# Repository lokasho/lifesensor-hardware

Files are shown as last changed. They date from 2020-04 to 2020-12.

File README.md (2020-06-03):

# lifesensor-hardware
Temporary repository for the next hardware generation of the CADUS Life Sensor.
Official repository at https://github.com/cadus/Life-Sensor.

## Similar projects and Resources:
- https://github.com/GliaX
- https://github.com/kitspace/awesome-electronics
- https://github.com/kitspace/kicad_footprints
- https://github.com/intajay/open-electronics

- ecg
    + https://github.com/xdever/MobilECG-II -> based on ADS1298
    + https://www.olimex.com/Products/Duino/Shields/SHIELD-EKG-EMG/open-source-hardware
    + https://www.electronicdesign.com/power-management/article/21798161/choose-the-right-resistors-for-medical-applications

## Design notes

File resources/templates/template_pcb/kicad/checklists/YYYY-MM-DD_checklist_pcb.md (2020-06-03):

# check list
- [ ] this file is a copy of ./YYYY-MM-DD_checklist_pcb.md with YYYY-MM-DD replaced by todays date.
- [ ] Updating the PCB from the schematic does not introduce changes. If errors/warnings can be ignored, list them here with a reason why.
- [ ] The DRC report has been saved to ../manufacture/gerbers/COMPONENT_VARIANT_PCBNAME.rpt
- [ ] All remaining unconnected items in the DRC report are followed by a line starting witht "Accepted: ... ", explaining why the connection can be ignored.
- [ ] All remaining error messages in the DRC report are followed by a line starting witht "Accepted: ... ", explaining why the error/warning can be ignored.
- [ ] The full board name equals the .kicad_pcb file name without the extension and is visibly placed on one outer copper layer.
- [ ] The board revision is visibly placed on one outer copper layer.
- [ ] The board revision major is equal to the design revision of the schematics
- [ ] The board revision minor has been incremented compared to the last board release or is one if this is the first release (last: , now: )
- [ ] The footprints have been archived to ../lib_footprint.pretty after the pcb has been edited the last time (FILE -> Archive Footprints -> Archive Footprints to Existing Library. Then choose lib_footprint)
- [ ] The drill and drill map files have been saved to ../manufacture/gerbers
- [ ] The gerber files of all necessary layers have been plotted to ../manufacture/gerbers
- [ ] The board has been exported as .svg file to ../manufacture/images with the following settings:
    - select all layers that are exported es gerber files
    - Print Mode: Color
    - svg page size: "Board area only"
    - Pagination: All layers in a single file

# change log
| date       | revision | author (github name) | description                  |
|:-----------|:---------|:---------------------|:-----------------------------|
| 2020-04-26 | 1        | lokash               | Created checklist            |
| 2020-04-27 | 2        | lokash               | Improved error report checks |
| 2020-04-27 | 3        | lokash               | Export layout as svg         |

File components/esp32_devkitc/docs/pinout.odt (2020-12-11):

# ESP32 DEVKITC Pinout

### Inputs/ External Interrupts

SENS_INT_BPM, SENS_INT_SPO2, SENS_INT_ECG

DISP_INT_TOUCH

### Outputs

~SENS_RST_ECG, ~SENS_RST_BPM, ~SENS_RST_SPO2

~SENS_CS_ECG, ~SENS_CS_BPM,~SENS_CS_SPO2

DISP_CS_DISP, DISP_CS_TOUCH

### Display BUS on VSPI (speed optimized)

DISP_MOSI, DISP_MISO, DISP_SCLK

### Debug

JTAG_~TRST, JTAG_TMS, JTAG_TCK, JTAG_TDI, JTAG_TDO

### PROC

PROC_SDA, PROC_SCL

## External GPIOs via I2C GPIO Expander

SENS_START, EXPGPIO1, EXPGPIO2, EXPGPIO3, EXPGPIO4, EXPGPIO5, EXPGPIO6, EXPGPIO7

|GPIO|Input|Output|Notes|Function|

|0|pulled up|OK|outputs PWM signal at boot, is pulled high|~SENS_CS_BPM|

|1|TX pin|OK|debug output at boot ||

|2|OK|OK|Needs to be floating while being flashed; |~SENS_CS_ECG|

|3|OK|RX pin|HIGH at boot |DISP_CS_TOUCH|

|4|OK|OK||~SENS_CS_SPO2|

|5|OK|OK|outputs PWM signal at boot,VSPI_CS |DISP_CS_DISP|

|6|x|x|connected to the integrated SPI flash||

|7|x|x|connected to the integrated SPI flash||

|8|x|x|connected to the integrated SPI flash||

|9|x|x|connected to the integrated SPI flash||

|10|x|x|connected to the integrated SPI flash||

|11|x|x|connected to the integrated SPI flash||

|12|OK|OK|boot fail if pulled high;MTDI,HSPI_MISO|JTAG_TDI|

|13|OK|OK|MTCK, HSPI_MOSI|JTAG_TCK|

|14|OK|OK|outputs PWM signal at boot,MTMS, HSPI_CLK|JTAG_TMS|

|15|OK|OK|outputs PWM signal at boot,MTDO,HSPI_CS|JTAG_TDO|

|16|OK|OK||~SENS_RST_BPM|

|17|OK|OK||~SENS_RST_SPO2|

|18|OK|OK|VSPI_CLK|DISP_SCLK|

|19|OK|OK|VSP_MISO|DISP_MISO|

|21|OK|OK|I2C_SDA|PROC_SDA|

|22|OK|OK|I2C_SCL|PROC_SCL|

|23|OK|OK|VSPI_MOSI|DISP_MOSI|

|25|OK|OK||SENS_MOSI|

|26|OK|OK||SENS_MISO|

|27|OK|OK||SENS_SCLK|

|32|OK|OK||GPIOEXP_INT|

|33|OK|OK||~SENS_RST_ECG|

|34|OK||input only|SENS_INT_ECG|

|35|OK||input only|DISP_INT_TOUCH|

|36|OK||input only; SENSOR_VP|SENS_INT_BPM|

|39|OK||input only; SENSOR_VN|SENS_INT_SPO2|

|EN|||Connected to RTS, DTR reset circuit|JTAG_~TRST|

|3V3|||3.3V|SENS_3V3_DIG|

|EXT_5V||||5V_in|

|GND1,2,3|||GND|GND|

Orange Pins are strapping pins.

convert table to text with | as separator to paste into github

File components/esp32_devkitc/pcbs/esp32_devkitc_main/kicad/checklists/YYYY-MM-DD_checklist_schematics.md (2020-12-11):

# hints
1. All paths are refered to the kicad project directory.

# check list

- [ ] this file is a copy of ./YYYY-MM-DD_checklist_schematics.md with YYYY-MM-DD replaced by todays date.
- [ ] No subschematic name contains blank spaces (both sheet name and subschematic file name)
- [ ] the date of all schematic pages info is the the date of the last schematic edit
- [ ] the command `python ../../../../../resources/scripts/archive_symbols.py esp32_devkitc_main.pro` has been run to move all schematic symbols to the local library
- [ ] The design revision has been incremented compared to the last release (last: , now: )
- [ ] The ERC report has been saved to ../manufacture/schematics/esp32_devkitc_main.erc
- [ ] All remaining error messages in the ERC report are followed by a line starting with "Accepted: ... ", explaining why the error/warning can be ignored.
- [ ] The schematics have been plotted into ../manufacture/schematics/esp32_devkitc_main.pdf after the last edit.

# change log

| date       | revision | author (github name) | description                                |
|:-----------|:---------|:---------------------|:-------------------------------------------|
| 2020-04-26 | 1        | lokash               | Created checklist                          |
| 2020-04-27 | 2        | lokash               | Improved error report checks and add hints |
| 2020-04-28 | 3        | lokash               | Improved schematics plotted check          |
| 2020-04-29 | 4        | lokash               | Fixed project name templates               |
| 2020-08-25 | 5        | lokash               | include experiences from ecg_ads1292       |

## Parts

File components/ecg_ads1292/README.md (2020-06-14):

# lifesensor ecg_ads1292
The lifesensor ecg_ads1292 component provides a [ECG](https://en.wikipedia.org/wiki/Electrocardiography) frontent based on Texas Instruments [ADS1292](http://www.ti.com/lit/ds/symlink/ads1292.pdf).

WARNING: THIS COMPONENT DOES NOT PROVIDE ANY PROTECTION AGAINST ELECTRICAL SHOCKS! ALWAYS USE APPROPRIATE MEDICAL APPROVED POWER SUPPLIES! USE AT YOUR OWN RISK!

## Objectives
This component is developed to quickly provide a first ECG sensor that can deliver reference data for comparison with other self-developed and possibly cheaper ECG frontends. It will also provide the possibility to test other (software) components like the pulse detection and the lifesensors [sensor bus](../system/lifesensor_system.svg) with real data.
<!-- TODO: link to sensor bus description -->

To minimize the development effort integrated circuits that include all needed analog circuitry are chosen. The ADS1292 is chosen because in a search it was the cheapest one that can provide a three channel ECG found.

Due to the prototype characteristics the development of the ecg_ads1292 compontent is not focusing on low prizes, availability or repairability.

## Subcomponents

This component consists of one PCB [ecg_ads1292_main](pcbs/ecg_ads1292_main) and a [driver](firmware).

For a description of the development of the PCB see [pcbs/ecg_ads1292_main/docs/README.md](pcbs/ecg_ads1292_main/docs/README.md)

For a description of the driver see [firmware/README.md](firmware/README.md)

#### Board view
This is a view of the last released version of the board:

ecg_ads1292_main board view

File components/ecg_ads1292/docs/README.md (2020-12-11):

# lifesensor ecg_ads1292
This document describes the [ECG](https://en.wikipedia.org/wiki/Electrocardiography) component based on Texas Instruments integrated ECG front end [ADS1292](http://www.ti.com/lit/ds/symlink/ads1292.pdf).

**WARNING: THIS CIRCUIT DOES NOT PROVIDE ANY PROTECTION AGAINST ELECTRICAL SHOCKS! ALWAYS USE APPROPRIATE MEDICAL APPROVED POWER SUPPLIES! USE AT YOUR OWN RISK!**

---

## Objectives
This component is developed to quickly provide a first ECG sensor that can deliver reference data for comparison with other self-developed and possibly cheaper ECG frontends. It will also provide the possibility to test other (software) components like the pulse detection and the lifesensors sensor bus with real data.

## Features
To be continued.
<!-- TODO: add ecg_ads1292 features -->

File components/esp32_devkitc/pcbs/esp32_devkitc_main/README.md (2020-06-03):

This is the kicad project directory template for a single pcb.
Its structure is inspired by https://hackaday.com/2017/05/18/kicad-best-practises-library-management/

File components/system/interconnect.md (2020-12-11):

<# Interconnect

The interconnect is the main bus between the PCBs of the different components of the lifesensor.
It is based on the 40-pin Raspberry Pi header.

The idea is to use the Raspberry Pi as a test platform for all components.

Pins with numbers higher than 26 are reserved and should therefore be left unconnected.

**ATTENTION: The Raspberry Pi can only deliver 30mA at the 3.3V rail and 300mA at the 5V rail.**

| Pin| RaspberryPi      | LifeSensor       | Pin| RaspberryPi        | LifeSensor      |
|  -:| :--------------- | :--------------- | -: | :----------------- | :---------      |
| 1  | 3V3 power        | SENS_3V3_ANA     | 2  | 5V power           | SENS_5V_ANA     |
| 3  | GPIO2 (SDA)      | SDA              | 4  | 5V power           | SENS_5V_ANA     |
| 5  | GPIO3 (SCL)      | SCL              | 6  | GND                | GND             |
| 7  | GPIO4 (GPCLK0)   | SENS_BPM_DRDY    | 8  | GPIO14 (TXD)       | SENS_IO0        |
| 9  | GND              | GND              | 10 | GPIO15 (RXD)       | SENS_IO1        |
| 11 | GPIO17           | SENS_ECG_DRDY    | 12 | GPIO18 (PCM_CLK)   | SENS_SPO2_DRDY  |
| 13 | GPIO27           | SENS_START       | 14 | GND                | GND             |
| 15 | GPIO22           | SENS_RST_BPM_n   | 16 | GPIO23             | SENS_RST_ECG_n  |
| 17 | 3V3 power        | SENS_3V3_DIG     | 18 | GPIO24             | SENS_RST_SPO2_n |
| 19 | GPIO10 (MOSI)    | SENS_MOSI        | 20 | GND                | GND             |
| 21 | GPIO9 (MISO)     | SENS_MISO        | 22 | GPIO25             | SENS_CS_BPM_n   |
| 23 | GPIO11 (SCLK)    | SENS_SCLK        | 24 | GPIO8 (CE0)        | SENS_CS_ECG_n   |
| 25 | GND              | GND              | 26 | GPIO7 (CE1)        | SENS_CS_SPO2_n  |
| 27 | GPIO0 (ID_SD)    | RESERVED         | 28 | GPIO1 (ID_SC)      | RESERVED        |
| 29 | GPIO5            | RESERVED         | 30 | GND                | GND             |
| 31 | GPIO6            | RESERVED         | 32 | GPIO12 (PWM0)      | RESERVED        |
| 33 | GPIO13 (PWM1)    | RESERVED         | 34 | GND                | GND             |
| 35 | GPIO19 (PCM_FS)  | RESERVED         | 36 | GPIO16             | RESERVED        |
| 37 | GPIO26           | RESERVED         | 38 | GPIO20 (PCM_DIN)   | RESERVED        |
| 39 | GND              | GND              | 40 | GPIO21 (PCM_DOUT)  | RESERVED        |

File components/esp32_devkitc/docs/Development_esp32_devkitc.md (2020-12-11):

# Development of esp32_devkitc

## System interfaces of the esp32 component

The following figure shows the connections between the different components of the lifesensor:
System 
The esp32 component is in the middle of the graph and
has four interfaces:

- The **power bus** towards the power component,
- the **sensor bus** towards the ecg, spo2, and bp components,
- the **display bus** towards a possible small internal display, and
- the **processor bus** towards an Raspberry Pi that may drive a bigger internal or external display

The following sections describe each interface in more detail.
### Power bus
The esp32 component is provided with a 5V from the power component.
The esp32 component then provides a digital and a analog 3.3V rail, as well as a analog 5V rail and distributes these rails to components on the sensor and display bus.

In order to be able to use simple power circuits both the output current 
of the provided rails is limited 
- to 200mA for the analog 5V rail,
- to 150mA for the analog 3.3V rail, and
- to 50mA for the digital 3.3V rail.

If this limit is exceeded, some of the components must directly use the 5V supply from the main power component and generate their own rails if needed. (See power component for limits of that rail.)

The DevKit-C uses a ESP32-Wroom which requires 500mA from a 3.3V rail.
The 3.3V power rail is provided by the DevKit-C itself with a AMS1117-3.3 LDO that can deliver up to 1A. This is sufficient to power the ESP32-Wroom and the 200mA for external components.

The maximum total input current of the 5V power rail then calculates to
$$
I_{5V, in, max} = \overbrace{500mA}^{ESP32-Wroom} + \overbrace{200mA}^{3.3V extern} + \overbrace{200mA}^{5V extern} = 900mA
$$

For the 5V input and analog rails a broad range of 4.5V to 5.5V is allowed.
For the 3.3V analog and digital output rails a closer range between 3.2V and 3.3V must be provided.

### Sensor bus
The sensor bus is part of the main interconnect, which is described in more detail in [/components/system/interconnect.md](../../system/interconnect.md).

It is based on the Raspberry Pi HAT connector and provides
- analog 5V power rail (provided by the esp32 component)
- analog 3.3V power rail (provided by the esp32 component)
- digital 3.3V power rail (provided by the esp32 component)
- SPI bus 
  - with three chip select lines for the three sensors (SENS_CS_ECG_n, SENS_CS_SPO2_n, SENS_CS_BPM_n)
  - esp32 component is master
  - might be shared with esp32 display SPI bus via jumper (excluding chip select signals)
- a reset signal for each sensor (SENS_RST_ECG_n, SENS_RST_SPO2_n, SENS_RST_BPM_n)
- one start signal for all sensors
- an interrupt line for each sensor (SENS_ECG_DRDY, SENS_SPO2_DRDY, SENS_BPM_DRDY)
- two GPIO lines that can be used for signals between the esp32 component and costum sensors (SENS_IO0, SENS_IO1)
- an I2C bus (SENS_SDA, SENS_SCL)
  - that might be used by the processor bus (jumper/solder bridge on ESP32 component)

### Internal display bus
The Internal display bus provides the possibility to connect a display with low resolution directly to the stm32.
For this the following signals/rails are provided
- 5V or 3.3V power rail (switchable per jumper/solder bridge on ESP32 component)
- SPI bus with 
  - two chip selects for display and touch sensor (INTDISP_CS_DISP_n, INTDISP_CS_TOUCH_n)
  - ESP32 is master
  - might be shared with sensor SPI bus via jumper (excluding chip select signals)
  - an interrupt signal for the touch sensor (INTDISP_ISR_TOUCH)

### Processor bus
The processor bus is a single I2C bus with the ESP32 module as master and the
RPi as slave. The I2C bus is
- has signals PROC_SDA and PROC_SCL
- might use the interconnect (jumper/solder bridge on ESP32 component)

## Other connections of the esp32 component
Besides the four interfaces to other system components, the esp32 component needs other connectors, which are described in the following sections.

### JTAG Header
A 20 pin ARM JTAG header is connected according to https://raw.githubusercontent.com/gojimmypi/ESP32/master/images/myESP32%20DevKitC%20pinout.png

| DevKitC Pin | JTAG signal  | header pin |
|---|---|---|
| 3V3  | VTref | 1 |
| EN | nTRST | 5 |
| IO12 | TDI | 8 |
| IO14 | TMS | 10 |
| IO13 | TCK | 4 |
| (GND) | RTCK | 11 |
| IO15 | TDO | 6 | 
| GND  | GND | 3,9 (7)|

---
# ESP32 DEVKITC Pinout

### Inputs/ External Interrupts
SENS_INT_BPM, SENS_INT_SPO2, SENS_INT_ECG  
DISP_INT_TOUCH 

### Outputs
~SENS_RST_ECG, ~SENS_RST_BPM, ~SENS_RST_SPO2
~SENS_CS_ECG, ~SENS_CS_BPM,~SENS_CS_SPO2 
DISP_CS_DISP, DISP_CS_TOUCH  

### Display BUS on VSPI (speed optimized) 
DISP_MOSI, DISP_MISO, DISP_SCLK 

### Debug 
JTAG_~TRST, JTAG_TMS, JTAG_TCK, JTAG_TDI, JTAG_TDO

### PROC
PROC_SDA, PROC_SCL

## External GPIOs via I2C GPIO Expander
SENS_START, EXPGPIO1, EXPGPIO2, EXPGPIO3, EXPGPIO4, EXPGPIO5, EXPGPIO6, EXPGPIO7 

|GPIO|Input|Output|Notes|Function|
|---|---|---|---|---|
|0|pulled up|OK|outputs PWM signal at boot, is pulled high|~SENS_CS_BPM|
|1|TX pin|OK|debug output at boot ||
|2|OK|OK|Needs to be floating while being flashed; |~SENS_CS_ECG|
|3|OK|RX pin|HIGH at boot |DISP_CS_TOUCH|
|4|OK|OK||~SENS_CS_SPO2|
|5|OK|OK|outputs PWM signal at boot,VSPI_CS |DISP_CS_DISP|
|6|x|x|connected to the integrated SPI flash||
|7|x|x|connected to the integrated SPI flash||
|8|x|x|connected to the integrated SPI flash||
|9|x|x|connected to the integrated SPI flash||
|10|x|x|connected to the integrated SPI flash||
|11|x|x|connected to the integrated SPI flash||
|12|OK|OK|boot fail if pulled high;MTDI,HSPI_MISO|JTAG_TDI|
|13|OK|OK|MTCK, HSPI_MOSI|JTAG_TCK|
|14|OK|OK|outputs PWM signal at boot,MTMS, HSPI_CLK|JTAG_TMS|
|15|OK|OK|outputs PWM signal at boot,MTDO,HSPI_CS|JTAG_TDO|
|16|OK|OK||~SENS_RST_BPM|
|17|OK|OK||~SENS_RST_SPO2|
|18|OK|OK|VSPI_CLK|DISP_SCLK|
|19|OK|OK|VSP_MISO|DISP_MISO|
|21|OK|OK|I2C_SDA|PROC_SDA|
|22|OK|OK|I2C_SCL|PROC_SCL|
|23|OK|OK|VSPI_MOSI|DISP_MOSI|
|25|OK|OK||SENS_MOSI|
|26|OK|OK||SENS_MISO|
|27|OK|OK||SENS_SCLK|
|32|OK|OK||GPIOEXP_INT|
|33|OK|OK||~SENS_RST_ECG|
|34|OK||input only|SENS_INT_ECG|
|35|OK||input only|DISP_INT_TOUCH|
|36|OK||input only; SENSOR_VP|SENS_INT_BPM|
|39|OK||input only; SENSOR_VN|SENS_INT_SPO2|
|EN|||Connected to RTS, DTR reset circuit|JTAG_~TRST|
|3V3|||3.3V|SENS_3V3_DIG|
|EXT_5V||||5V_in|
|GND1,2,3|||GND|GND|

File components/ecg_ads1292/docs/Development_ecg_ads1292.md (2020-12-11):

# Development lifesensor ecg_ads1292

## Requirements and constraints
To minimize the development effort integrated circuits that include all needed analog circuitry are chosen. The ADS1292 is chosen because in a search it was the cheapest one that can provide a three channel ECG.
Due to the prototype characteristics the development of the ecg_ads1292 compontent is not focusing on low prizes, availability or repairability.

## Subcomponents
This component consists of one PCB [ecg_ads1292_main](../pcbs/ecg_ads1292_main) and a [driver](../code).

## PCB ecg_ads1292_main Rev. 0

### Schematics
The schematics can be found in 
../pcbs/ecg_ads1292_main/manufacture/schematics

The main sources for the circuit design are
- the ADS1292 data sheet: http://www.ti.com/lit/ds/symlink/ads1292.pdf
- TI Bio-Signal Monitor Reference Design: https://www.ti.com/tool/TIDM-BIOSIGNMONITOR
- the ADS1x9xECG-FE Demonstration Kit User's Guide: https://www.ti.com/lit/ug/slau384a/slau384a.pdf

The development of the circuits is straight forward as the ADS1292 only needs a few passive components and an optional LDO for the analog frontend, and a few others for connecting it to the [sensor bus](../../system/interconnect.md). Most components can be directly derived from the data sheet or the other links given above.

Nevertheless the following  will describe the circuits and components that differ from the references.

#### Analog input section
The input filter of the analog inputs IN1 to IN3 of the ADS1292R was derived from the Texas Instruments [demo board](http://www.ti.com/tool/TIDM-BIOSIGNMONITOR).
The input resistors R9 to R22 values have been decreased from 51kΩ to 22kΩ to compensate for the external defibrillator input protection.
Also the circuit has been changed so that each of three leads of the Einthoven triangle can be directly conected to one of the three input channels.
(Note however that only two leads can be measured directly, as the ADS1292 only comprises two ADCs. The third lead can be calculated from the other two).
The reason is, that if one electrode is torn off, the software can always switch to an input that is connected to the remaining two electrodes.
This way at least one valid lead can be measured in this case.

#### Right leg driver (*1*)
The wiring of the right-leg driver has also been adapted from th demo board. 
The Right-Leg-Driver is an OPV integrated in the ADS1292R, whose output (pin 30) is connected to an electrode on the patient via a resistor that will be included with the defibrillator protection. 
Therefore on this board the limiting output resistor was omitted.
To make the RLD compliant to the current limits (body floating, single fault codition -> max. 50µA DC according to wikipedia) an 100kΩ resistor R13 is inserted at the OPA output. On the demo board a 0Ω bridge is used at this point.
The idea for the circuit modification was taken from the Texas Instruments application report 'Improving Common-Mode Rejection Using the Right-Leg DriveAmplifier' ( www.ti.com/lit/an/sbaa188/sbaa188.pdf ). So if RLDOUT should be fully driven in case of an error, the output current is still limited by R13.
Due to the characteristics of the OPV, the potential between the resistors, i.e. at the connectors RLD output, is the same in both cases.
Since it is determined solely by the resistor R12 connected to the inverting input RLDINV.
In the real circuit, this means that the output of the OPV needs higher output voltage swing and has higher distortions.
Since the output current of the OPV is usually 1μA according to the Application Report, R13 leads to an additional voltage swing of 0.1V in the present circuit.
The disadvantages mentioned above should therefore be negligible.
As a result, the output impedance of the right-leg driver can be lowered.
It can be assumed that this will result in a higher cut-off frequency and a better response of the right-leg driver.

#### Analog power supply
To keep the analog power supply as quiet as possibly during prototyping and testing an additional LDO is inserted.
This can be ommitted after testing.

#### Analog frontend connection
The analog frontend will be connected to an external defibrillator protection circtuit.
To keep the ground connection between the two PCBs flexible the GND pins of Connector J1 have their own GNDPWR net, which can be connected to the GND net via several solder bridges at different points.

#### Sensor bus connection

A few notes about the sensor bus connection:
- no external Clock is required, therfore the CLKSEl pin is pulled high and the CLK pin is left unnconnected
- The GPIOs are not needed. The data sheet recommends to pull them down, which is down with two 6.8kΩ resistors.
- All digital output signals have a 100Ω series resistor to improve EMI. 
  TODO: evaluate signal quality in real environment.

The following list describes the nets of the sensor bus this component accesses.

**Power**

| Label           | Pin| Pi Header          |
|:----------------|:---|:-------------------|
| SENS_5V_ANA     | 2  | 5V power           |
| SENS_3V3_DIG    | 17 | 3V3 power          |

**Signals**

| Label           | Pin| Pi Header          |
|:----------------|:---|:-------------------|
| SENS_ECG_DRDY   | 11 | GPIO17             |
| SENS_START      | 13 | GPIO27             |
| SENS_RST_ECG_n  | 16 | GPIO23             |
| SENS_MOSI       | 19 | GPIO10 (MOSI)      |
| SENS_MISO       | 21 | GPIO9 (MISO)       |
| SENS_SCLK       | 23 | GPIO11 (SCLK)      |
| SENS_CS_ECG_n   | 24 | GPIO8 (CE0)        |

- **SENS_ECG_DRDY** Data ready. Is pulled down by the ADS1292 when a new sample has been taken. -> **ESP:** Interrupt on the falling edge, that triggers fetching the sample via SPI bus.
- **SENS_START** After configuring the continuos conversion mode the ADS129 starts sampling, when this signal is pulled HIGH. -> **ESP:** output push pull
- **SENS_RST_ECG_n** After system start the ADS1292 needs two reset pulses by driving this signal LOW. **ESP:** output push pull
- **SENS_MOSI** SPI bus
- **SENS_MISO** SPI bus
- **SENS_SCLK** SPI bus clock, maximum frequency is twice the ADS1292 base clock, so 1.024MHz when running on the internal 512kHz clock. **ESP:** (clock polarity: low, phase: second edge)
- **SENS_CS_ECG_n** SPI chip select for the ECG (no inter byte pulses, after transmitting data, this signal must not be driven HIGH agian to fast, see data sheet for SPI timing constraints)

### Layout

The constraints for the layout are
- 2 Layer
- best signal quality
- form factor (maximum) and mounting holes for RPi HAT:

<p>

(see sensor stack)

</p>

---

The board is not intended to be etched by a maker space or hobbyist, therefore vias and small structures can be used.
For the layout the hints in the datasheet are followed.
It states that the GND plane could be split, if the star point is at the ADS1292, but in general this is not neccessary with correct component placement and routing.
In this case a split is done, to keep the analog GND plane small to avoid coupling as the environement is not yet known.

Here is a view of the layout:
<p>
layout of ecg_ads1292_main
</p>

(*1*) This section is based on the translation of a project documentation at Technische Universität Berlin

### Start-up of first prototypes Rev. 0.1

Two prototypes have been produced July 2020.
As no LDO where ordered the analog supply voltage is directly using the 5V from the interconnect. This is done by shorting the appropriate pads for the LDO. (The ADS1292 allows the analog supply voltage to be 5V).

For the first tests a STM32 based NUCLEO-L476RG dev board was used.
Both power and digital signals where connected to that board.
The test program streams the data via UART to the included virtual serial port of the NUCLEO-L476RG which is connected to a PC.

To test the boards, the internal test signals of the ADS1292 are used.
With prototype 1 also a real ECG signal was successfully recorded.

#### Prototype 1
The tests show that the internal 2.4V reference voltage is not stable.
This leads to intermittent changes in the measured signal: at somw point they start to drift and sometimes saturate shortly just before recovering again.

After switching to the 4V reference these issues are gone. This is (only) possible because a 5V analog supply voltage is used.
This means that
**the 2.4V reference voltage of prototype 1 can not be used.**

While recording the real ECG signal the host PC (notebook) was detached from the mains adapter for safety reasons.
The result was visually ok. One channel had a little bit more noise which is due to the RLD input not beeing connected to one of the inputs of that channel. This can be improved at a later point.

#### Prototype 2
This device worked as expeceted.
But while testing the external analog input circuits, the signals saturated. The reason was, that the 2.4V internal reference was used, but the RLD pushes the potential to $V_{DDA} / 2 = 5V / 2 = 2.5V$, which is then outside  of the ADC range.
It should therefore be noted that, when using 5V as analog supply voltage, the internal reference voltage must be set to 4V or the RLD reference voltage must be supplied from an external voltage devider that provides a voltage below 2.4V (ideally 1.2V).

## ESP32 component driver 
The main IC ADS1292 needs to controlled from the ESP32 via SPI and several IO/interrupt lines.
The following describes the development of the driver.

To be continued.

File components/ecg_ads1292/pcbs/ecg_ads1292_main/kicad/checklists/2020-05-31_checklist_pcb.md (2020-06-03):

# check list
- [x] this file is a copy of ./YYYY-MM-DD_checklist_pcb.md with YYYY-MM-DD replaced by todays date.
- [x] Updating the PCB from the schematic does not introduce changes. If errors/warnings can be ignored, list them here with a reason why.
- [x] The DRC report has been saved to ../manufacture/gerbers/ecg_ads1292_main.rpt
- [x] All remaining unconnected items in the DRC report are followed by a line starting witht "Accepted: ... ", explaining why the connection can be ignored.
- [x] All remaining error messages in the DRC report are followed by a line starting witht "Accepted: ... ", explaining why the error/warning can be ignored.
- [x] The full board name equals the .kicad_pcb file name without the extension and is visibly placed on one outer copper layer.
- [x] The board revision is visibly placed on one outer copper layer.
- [x] The board revision major is equal to the design revision of the schematics
- [x] The board revision minor has been incremented compared to the last board release or is one if this is the first release (last: , now: 1)
- [x] The footprints have been archived to ../lib_footprint.pretty after the pcb has been edited the last time (FILE -> Archive Footprints -> Archive Footprints to Existing Library. Then choose lib_footprint)
- [x] The drill and drill map files have been saved to ../manufacture/gerbers
- [x] The gerber files of all necessary layers have been plotted to ../manufacture/gerbers
- [x] The board has been exported as .svg file to ../manufacture/images with the following settings:
    - select all layers that are exported es gerber files
    - Print Mode: Color
    - svg page size: "Board area only"
    - Pagination: All layers in a single file

# change log
| date       | revision | author (github name) | description                  |
|:-----------|:---------|:---------------------|:-----------------------------|
| 2020-04-26 | 1        | lokash               | Created checklist            |
| 2020-04-27 | 2        | lokash               | Improved error report checks |
| 2020-04-27 | 3        | lokash               | Export layout as svg         |

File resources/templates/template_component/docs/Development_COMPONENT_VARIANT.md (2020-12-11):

# Development lifesensor COMPONENT_VARIANT

This document describes the development process of the COMPONENT_VARIANT component.
From the paragraphs below the suggested design procedure can be derived.
But it is not a must follow. More important is a good documentation of each step.

Also important is the design revision number for PCBs, so that no one gets confused:
It consists of two numbers separated by a decimal dot, for example `0.1`.
The second number `1` is the minor. It is increased after a layout was released (i.e. a pcb was manufactured).
The first number `0` is the major. It is increased only if the schematic has been changed after the last release.
As the release number on the PCB must be adapted, increasing the major always requires also increasing the minor!
Both numbers are counting zero based, so the first released/manufactured prototype should have the revision `0.0`.

## Requirements and Constraints
This section describes the requirements and constraints for this component.
They might be derived from the objectives written in the README.md next to this file.

## Subcomponents
Explanation of how and why this component is split into subcomponents (With references to
the corresponding folders in the repo).
Ideally a diagram of all subcomponents is given, too.

## PCB COMPONENT_VARIANT_BOARDNAME Rev. 0
This section describes the design procedure of a single PCB for this component.
It should be repeated with all its subsections for every major revision of the PCB 
(i.e. when the schematic changed after a release).

### Schematics
This section should describe in detail how circuits where designed and how components 
where selected.
It also should highlight hints/constraints that will later be needed for the layout 
(For example when a high speed opamp needs the ground plane removed around it).

### Layout Rev. 0.1
This section should describe the layout decisions and confirm constraints from
the schematics or for the placement of certain components.

### Start-up of first prototypes Rev. 0.1
This section describes the start up procedure and findings of the first prototypes of this design revision.

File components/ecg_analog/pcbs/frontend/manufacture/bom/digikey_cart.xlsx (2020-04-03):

Index | Quantity | Part Number | Manufacturer Part Number | Description | Customer Reference | Available | Backorder | Unit Price | Extended Price USD
1 | 1 | 311-1.00MFRCT-ND | RC1206FR-071ML | RES SMD 1M OHM 1% 1/4W 1206 |  | 1 | 0 | 0.1 | 0.10
2 | 1 | 311-4449-1-ND | CC1206JRX7R9BB334 | CAP CER 0.33UF 50V X7R 1206 |  | 1 | 0 | 0.32 | 0.32
3 | 1 | 311-1.00KFRCT-ND | RC1206FR-071KL | RES SMD 1K OHM 1% 1/4W 1206 |  | 1 | 0 | 0.1 | 0.10
4 | 1 | 311-24.9KFRCT-ND | RC1206FR-0724K9L | RES SMD 24.9K OHM 1% 1/4W 1206 |  | 1 | 0 | 0.1 | 0.10
5 | 2 | P16.9KFCT-ND | ERJ-8ENF1692V | RES SMD 16.9K OHM 1% 1/4W 1206 |  | 2 | 0 | 0.1 | 0.20
6 | 2 | P4.30KFCT-ND | ERJ-8ENF4301V | RES SMD 4.3K OHM 1% 1/4W 1206 |  | 2 | 0 | 0.1 | 0.20
7 | 1 | 311-12.0KFRCT-ND | RC1206FR-0712KL | RES SMD 12K OHM 1% 1/4W 1206 |  | 1 | 0 | 0.1 | 0.10
8 | 6 | 311-40.2KFRCT-ND | RC1206FR-0740K2L | RES SMD 40.2K OHM 1% 1/4W 1206 |  | 6 | 0 | 0.1 | 0.60
9 | 1 | P1.27KFCT-ND | ERJ-8ENF1271V | RES SMD 1.27K OHM 1% 1/4W 1206 |  | 1 | 0 | 0.1 | 0.10
10 | 1 | 311-3.00KFRCT-ND | RC1206FR-073KL | RES SMD 3K OHM 1% 1/4W 1206 |  | 1 | 0 | 0.1 | 0.10
11 | 2 | 399-8131-1-ND | C1206C102J5RACTU | CAP CER 1000PF 50V X7R 1206 |  | 2 | 0 | 0.19 | 0.38
12 | 2 | 1276-1142-1-ND | CL31B223KBCNNNC | CAP CER 0.022UF 50V X7R 1206 |  | 2 | 0 | 0.14 | 0.28
13 | 2 | 311-4488-1-ND | CC1206KRX7R9BB563 | CAP CER 0.056UF 50V X7R 1206 |  | 2 | 0 | 0.27 | 0.54
14 | 1 | 311-4486-1-ND | CC1206KRX7R9BB124 | CAP CER 0.12UF 50V X7R 1206 |  | 1 | 0 | 0.27 | 0.27
15 | 1 | 296-41358-1-ND | OPA2377AIDR | IC OPAMP GP 2 CIRCUIT 8SOIC |  | 1 | 0 | 1.6 | 1.60
16 | 1 | 296-1283-1-ND | TL074CDR | IC OPAMP JFET 4 CIRCUIT 14SOIC |  | 1 | 0 | 0.5 | 0.50
17 | 1 | 296-30238-1-ND | INA826AIDR | IC INST AMP 1 CIRCUIT 8SOIC |  | 1 | 0 | 2.81 | 2.81
 |  |  |  |  |  |  |  |  | 8.30

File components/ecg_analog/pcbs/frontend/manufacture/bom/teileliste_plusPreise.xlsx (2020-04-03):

DIGIKEY: | Bestell-NR | Herstellerbezeichnung | Anzahl | Preis Einzel | Preis Gesamt
 | 296-41358-1-ND‎ | OPA2377AIDR‎ Texas Instruments IC OPAMP GP 2 CIRCUIT 8SOIC | 1 | 1.45 | 1.45
 | 296-30238-1-ND‎ | INA826AIDR‎ Texas Instruments IC INST AMP 1 CIRCUIT 8SOIC | 1 | 2.54 | 2.54
 | 311-4449-1-ND | CAP CER 0.33UF 50V X7R 1206 | 1 | 0.29 | 0.29
Reichelt: | RND 1206 1 1M | SMD-Widerstand, 1206, 1,0 MOhm, 250 mW, 1% | 1 | 0.02 | 0.02
 | RND 1206 1 1,0K | SMD-Widerstand, 1206, 1,0 kOhm, 250 mW, 1% | 1 | 0.02 | 0.02
 | X7R-G1206 22N | SMD-Vielschicht- Keramikkondensator 22N, 10% | 2 | 0.02 | 0.04
 | RND 1501206B4733 (https://www.reichelt.de/smd-kerko-1206-47-nf-50-v-10-mlcc-rnd-1501206b4733-p226023.html?) | SMD-Kerko, 1206, 47 nF, 50 V, 10%, MLCC | 2 | 0.02 | 0.04
 | KEM X7R1206 120N (https://www.reichelt.de/vielschicht-kerko-120nf-50v-125-c-kem-x7r1206-120n-p207153.html?) | Vielschicht-Kerko, 120nF, 50V, 125°C | 1 | 0.13 | 0.13
 | TL 074 CDRG4 (https://www.reichelt.de/operationsverstaerker-4-fach-so-14-tl-074-cdrg4-p188702.html?) | Operationsverstärker, 4-fach, SO-14 | 1 | 0.32 | 0.32
 | SMD 1/4W 4,3K (https://www.reichelt.de/smd-widerstand-1206-4-3-kohm-250-mw-5-smd-1-4w-4-3k-p18327.html?) | SMD-Widerstand, 1206, 4,3 kOhm, 250 mW, 5% | 2 | 0.04 | 0.08
 | RND 155HP06 BW (https://www.reichelt.de/smd-widerstand-1206-24-kohm-500-mw-1-rnd-155hp06-bw-p250886.html?) | SMD-Widerstand, 1206, 24 kOhm, 500 mW, 1% | 1 | 0.02 | 0.02
 | RND 155HP06 BC (https://www.reichelt.de/smd-widerstand-1206-16-kohm-500-mw-1-rnd-155hp06-bc-p250866.html?) | SMD-Widerstand, 1206, 16 kOhm, 500 mW, 1% | 2 | 0.02 | 0.04
 | RND 155HP06 AN (https://www.reichelt.de/smd-widerstand-1206-12-kohm-500-mw-1-rnd-155hp06-an-p250851.html?) | SMD-Widerstand, 1206, 12 kOhm, 500 mW, 1% | 1 | 0.02 | 0.02
 | RND 155HP06 CV (https://www.reichelt.de/smd-widerstand-1206-39-kohm-500-mw-1-rnd-155hp06-cv-p250911.html?) | SMD-Widerstand, 1206, 39 kOhm, 500 mW, 1% | 6 | 0.02 | 0.12
 | RND 155HP06 AR (https://www.reichelt.de/smd-widerstand-1206-1-3-kohm-500-mw-1-rnd-155hp06-ar-p250855.html?) | SMD-Widerstand, 1206, 1,3 kOhm, 500 mW, 1% | 1 | 0.02 | 0.02
 | KOA RK73H2BTTD31 (https://www.reichelt.de/smd-widerstand-1206-3-0-kohm-250-mw-1-koa-rk73h2bttd31-p238066.html?) | SMD-Widerstand, 1206, 3,0 kOhm, 250 mW, 1% | 1 | 0.02 | 0.02
 | RND 1501206N1029 (https://www.reichelt.de/smd-kerko-1206-1-nf-100-v-5-mlcc-rnd-1501206n1029-p226011.html?) | SMD-Kerko, 1206, 1 nF, 100 V, 5%, MLCC | 2 | 0.02 | 0.04
 | ZD 9,1 | Zenerdiode, 9,1 V, 1,3 W, DO-204AL/DO41 | 4 | 0.06 | 0.24
 |  |  |  |  | 5.45

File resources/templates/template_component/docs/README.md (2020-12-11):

# lifesensor COMPONENT_VARIANT
This section contains a one liner which describes this component/variant.
Also add potential risks using this device.

---

## Objectives
This section describes why this component/variant is beeing developed.

## Features
This section is intended to provide basic information for the end user (doctor).
As different variants of one component might have different features, this information 
can be used to quickly compile a manual/overview for the selected variants.

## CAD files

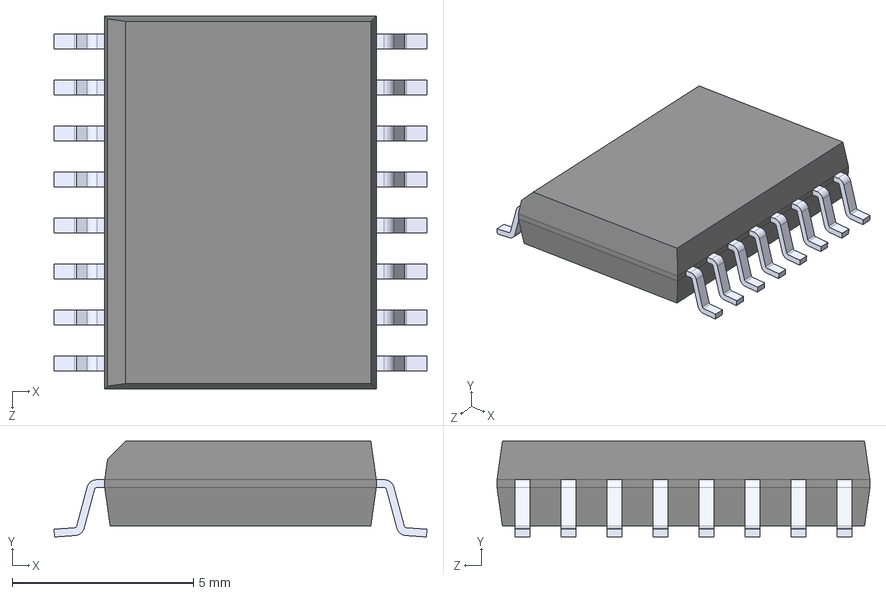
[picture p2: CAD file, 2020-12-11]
components/esp32_devkitc/pcbs/esp32_devkitc_main/kicad/lib_3d/PCF8574ADWR.step
10.3 x 2.65 x 10.3 mm

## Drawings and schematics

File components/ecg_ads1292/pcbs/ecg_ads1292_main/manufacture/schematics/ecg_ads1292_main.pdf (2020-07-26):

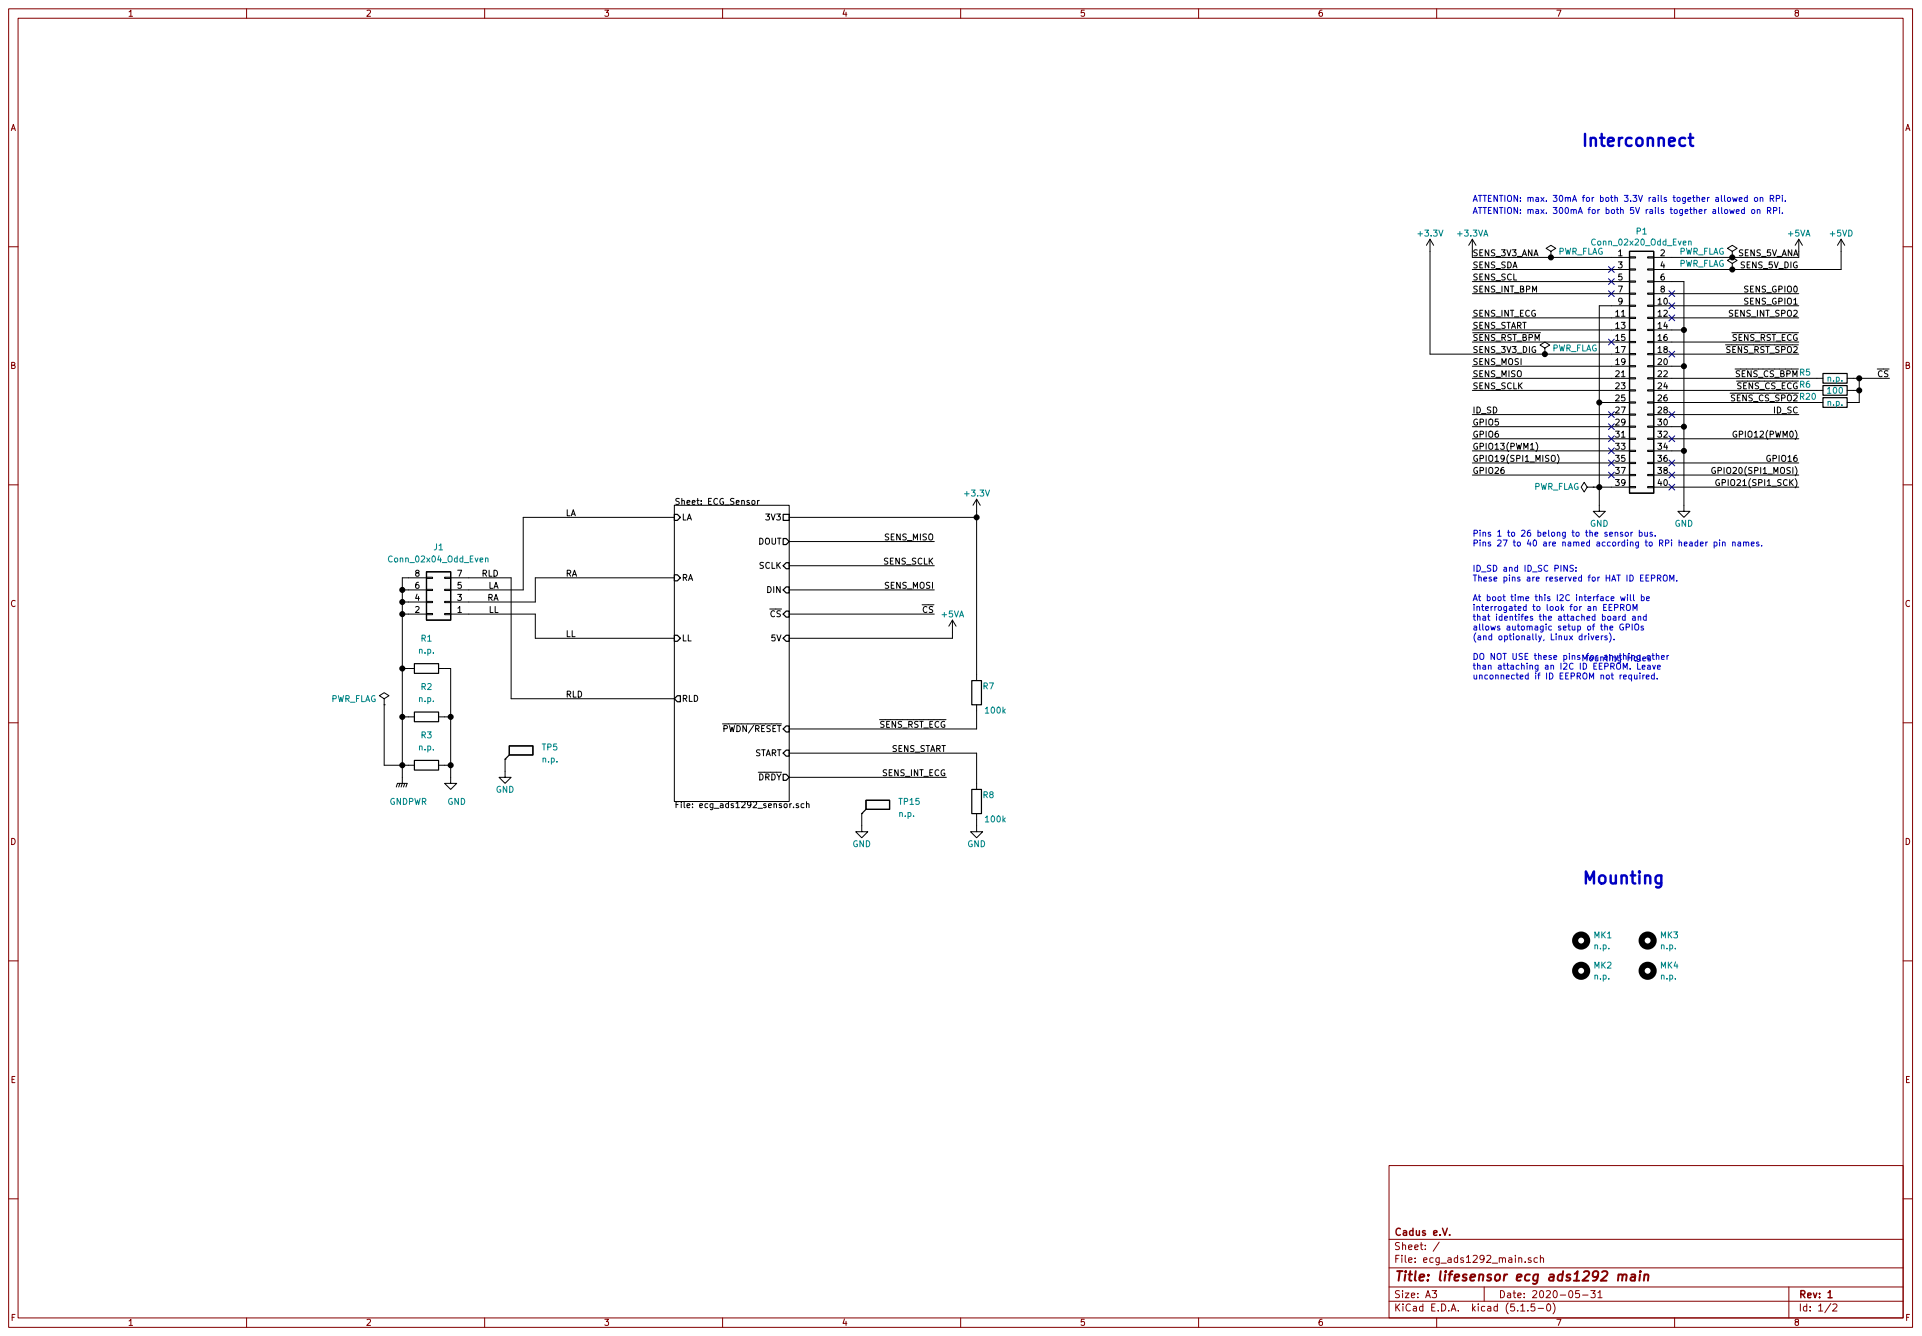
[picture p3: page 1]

ATTENTION: max. 30mA for both 3.3V rails together allowed on RPi.
ATTENTION: max. 300mA for both 5V rails together allowed on RPi.

29 | 30
31 | 32
33 | 34
35 | 36
37 | 38
39 | 40

Sheet: ECG_Sensor File: ecg_ads1292_sensor.sch
LARA
PWDN/RESET DOUT DRDY
START SCLK DIN

Pins 1 to 26 belong to the sensor bus.
Pins 27 to 40 are named according to RPi header pin names.

ID_SD and ID_SC PINS: These pins are reserved for HAT ID EEPROM. At boot time this I2C interface will be

interrogated to look for an EEPROM
that identifes the attached board and
allows automagic setup of the GPIOs
(and optionally, Linux drivers).

DO NOT USE these pins for anything other
than attaching an I2C ID EEPROM. Leave
unconnected if ID EEPROM not required.

File: ecg_ads1292_main.sch Sheet: / Cadus e.V.

Id: 1/2 Title: lifesensor ecg ads1292 main

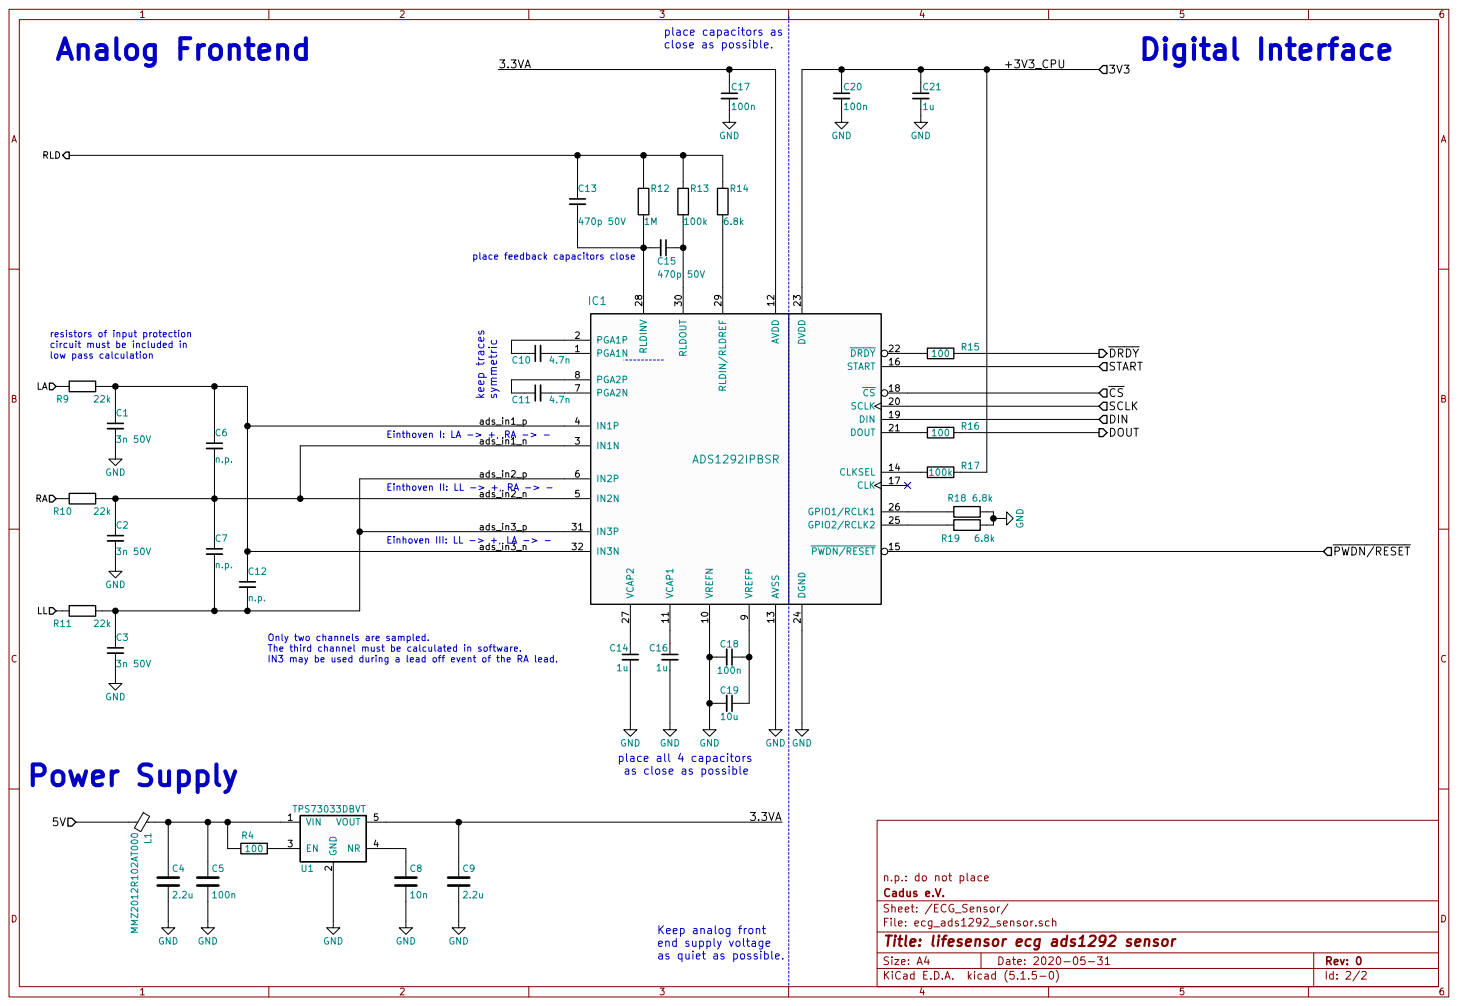
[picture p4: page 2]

place feedback capacitors close

resistors of input protection circuit must be included in

IN3 may be used during a lead off event of the RA lead.

place all 4 capacitors
as close as possible

Sheet: /ECG_Sensor/ Cadus e.V. n.p.: do not place

File: ecg_ads1292_sensor.sch
Id: 2/2 Title: lifesensor ecg ads1292 sensor

Keep analog front
end supply voltage
as quiet as possible.

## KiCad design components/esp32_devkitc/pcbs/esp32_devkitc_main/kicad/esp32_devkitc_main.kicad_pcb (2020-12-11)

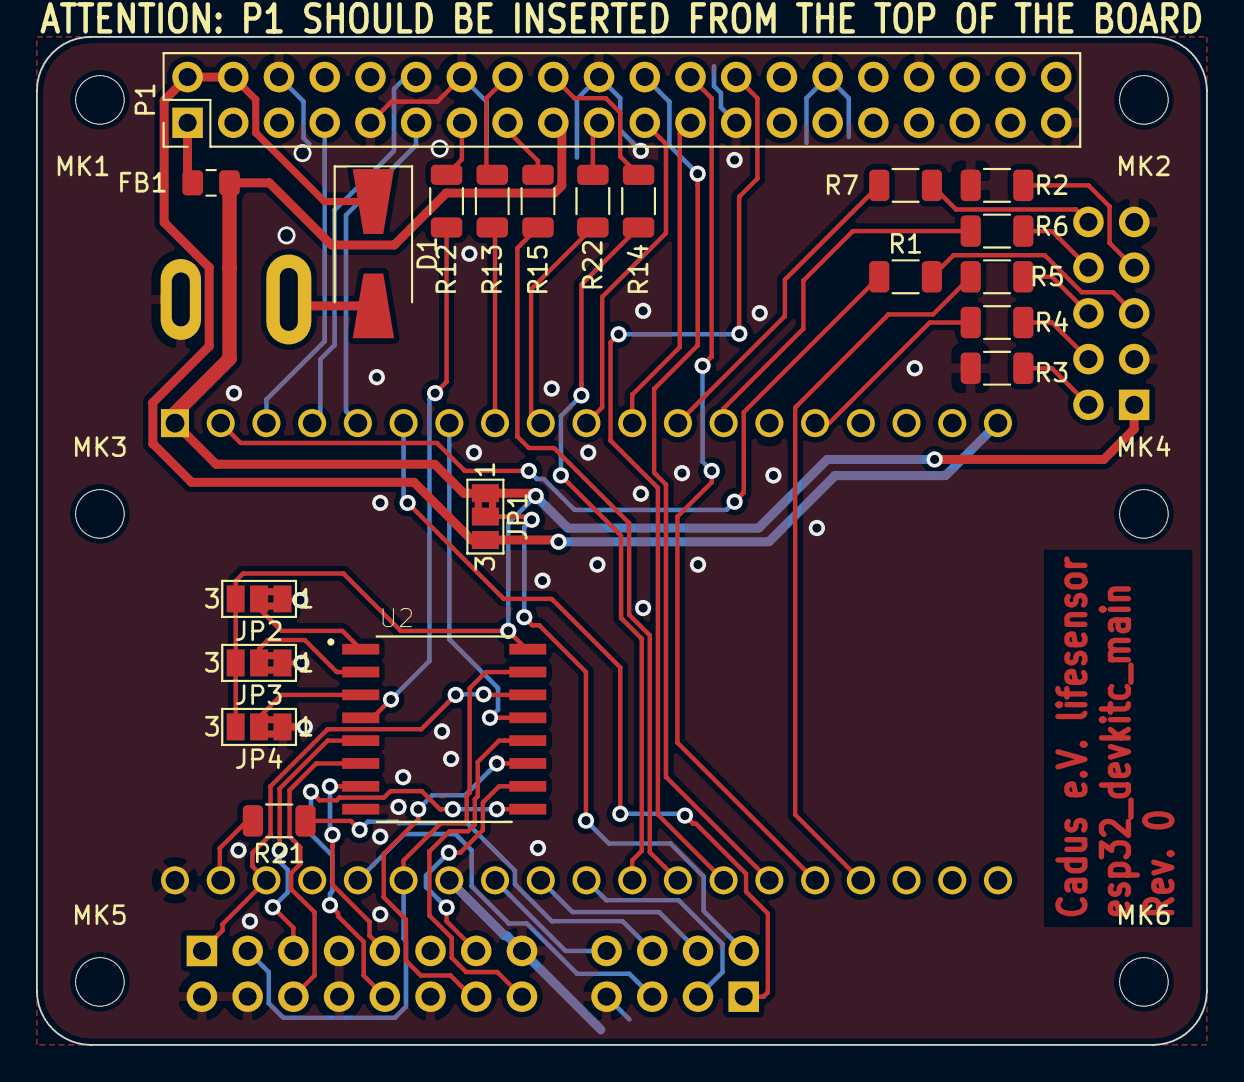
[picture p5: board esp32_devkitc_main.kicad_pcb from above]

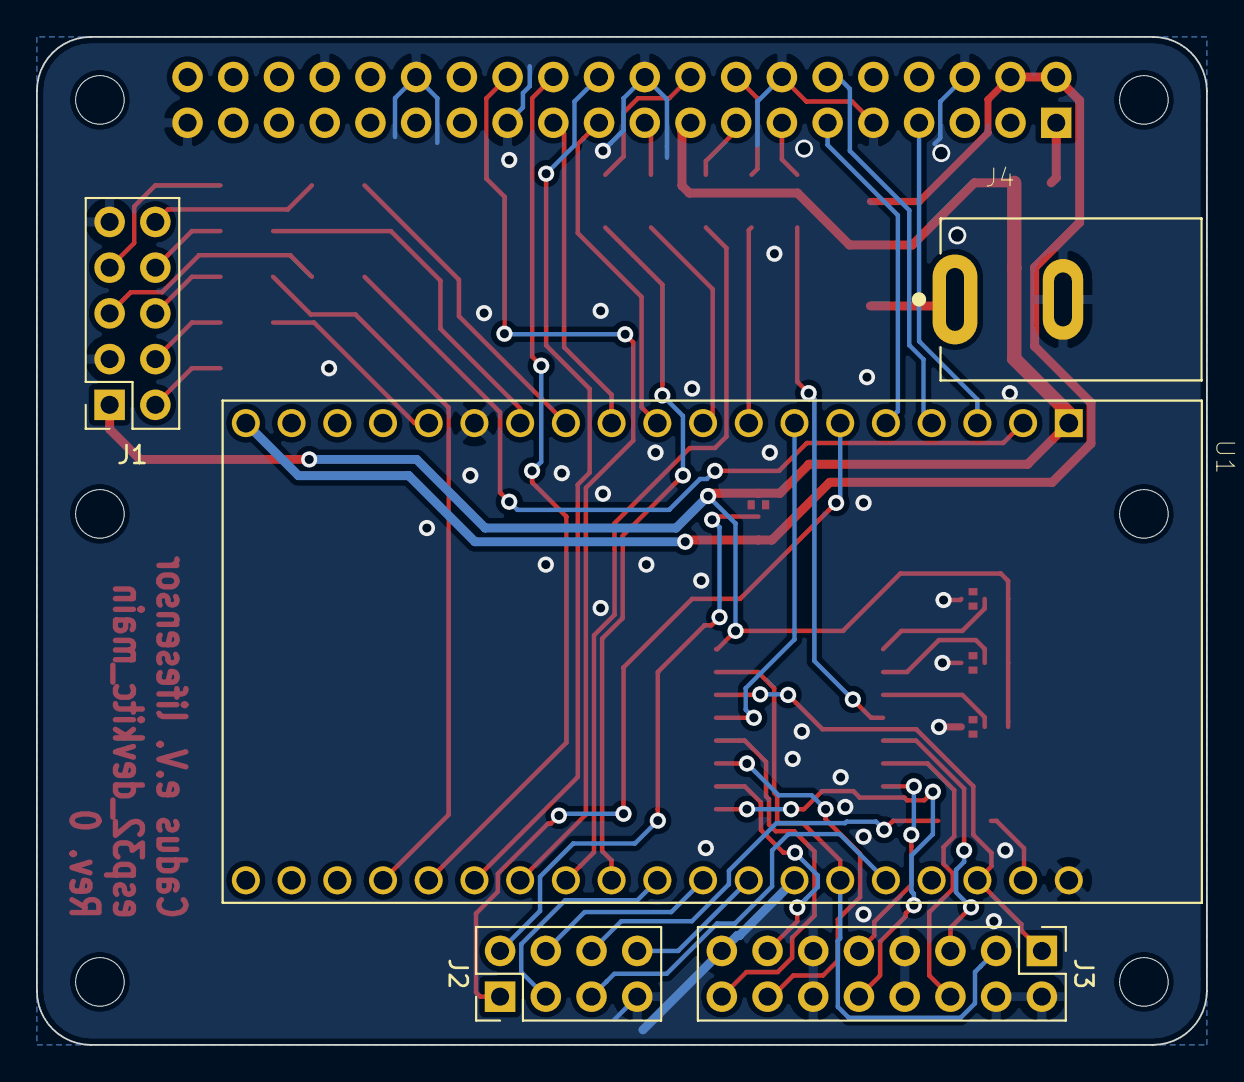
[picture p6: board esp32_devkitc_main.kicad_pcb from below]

Board: 2 copper layers, 65.0 x 56.0 mm, 32 parts (5 on the bottom side), 56 nets.

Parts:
D1: D; D_SMA-SMB_Universal_Handsoldering
FB1: Ferrite_Bead_Small; R_0805_2012Metric_Pad1.15x1.40mm_HandSolder
J1: Conn_02x05_Odd_Even; PinSocket_2x05_P2.54mm_Vertical
J2: Conn_02x04_Odd_Even; PinHeader_2x04_P2.54mm_Vertical
J3: Button/LED/I2C Connector; PinHeader_2x08_P2.54mm_Vertical
J4: CUI_PJ-102AH_Horizontal; CUI_PJ-037B
JP1, JP2, JP3, JP4: Jumper_NC_Dual; SolderJumper-3_P1.3mm_Bridged2Bar12_Pad1.0x1.5mm_NumberLabe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
MK1, MK2, MK3, MK4, MK5, MK6: M2.5; MountingHole_2.7mm_M2.5
P1: Conn_02x20_Odd_Even; PinHeader_2x20_P2.54mm_Vertical
R1, R3, R12, R13, R14, R15: 0; R_1206_3216Metric
R2: n.p.; R_1206_3216Metric
R4, R5, R6, R7, R21, R22: 100; R_1206_3216Metric
U1: ESP32-DEVKITC-32D; MODULE_ESP32-DEVKITC-32D
U2: PCF8574ADWR; SOIC127P1030X265-16N

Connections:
/5V_in: D1.2, J4.1
/DISP_CS_DISP: J2.3, U1.29
/DISP_CS_TOUCH: J2.5, U1.24
/DISP_INT_TOUCH: J2.1, U1.6
/DISP_MISO: J2.8, U1.27
/DISP_MOSI: J2.6, R21.1
/DISP_SCLK: J2.4, U1.28
/EXPGPIO1: J3.5, U2.5
/EXPGPIO2: J3.6, U2.6
/EXPGPIO3: J3.9, U2.7
/EXPGPIO4: J3.10, U2.9
/EXPGPIO5: J3.13, U2.10
/EXPGPIO6: J3.14, U2.11
/EXPGPIO7: J3.16, U2.12
/GPIOEXP_INT: U1.7, U2.13
/JTAG_RTCK: J1.2, R3.2
/JTAG_TCK: R4.1, U1.15
/JTAG_TDI: R6.1, U1.13
/JTAG_TDO: R5.1, U1.35
/JTAG_TMS: R7.1, U1.12
/JTAG_~SRST: J1.7, R2.1
/JTAG_~TRST: R1.1, U1.2
/PROC_SCL: J3.1, U1.22, U2.14
/PROC_SDA: J3.3, U1.25, U2.15
/SENS_3V3_ANA: FB1.2, P1.1
/SENS_3V3_DIG: FB1.1, J1.1, JP1.1, JP2.3, JP3.3, JP4.3, P1.17, U1.1, U2.16
/SENS_5V_ANA: D1.1, JP1.3, P1.2, P1.4, U1.19
/SENS_INT_BPM: P1.7, U1.3
/SENS_INT_ECG: P1.11, U1.5
/SENS_INT_SPO2: P1.12, U1.4
/SENS_MISO: P1.21, U1.10
/SENS_MOSI: P1.19, R22.1
/SENS_SCLK: P1.23, U1.11
/SENS_START: P1.13, R12.2
/~SENS_CS_BPM: P1.22, U1.33
/~SENS_CS_ECG: P1.24, U1.34
/~SENS_CS_SPO2: P1.26, U1.32
/~SENS_RST_BPM: P1.15, R15.2
/~SENS_RST_ECG: P1.16, R13.2
/~SENS_RST_SPO2: P1.18, R14.2
GND: J1.3, J1.9, J2.7, J3.2, J3.4, J3.7, J3.8, J3.11, J3.12, J3.15, J4.2, JP2.1, JP3.1, JP4.1, P1.6, P1.9, P1.14, P1.20, P1.25, P1.30, P1.34, P1.39, R2.2, R3.1, U1.14, U1.20, U1.26, U2.8
unnamed: J1.4, R4.2
unnamed: J1.5, R1.2
unnamed: J1.6, R5.2
unnamed: J1.8, R6.2
unnamed: J1.10, R7.2
unnamed: J2.2, JP1.2
unnamed: JP2.2, U2.1
unnamed: JP3.2, U2.2
unnamed: JP4.2, U2.3
unnamed: R12.1, U2.4
unnamed: R13.1, U1.8
unnamed: R14.1, U1.30
unnamed: R15.1, U1.31
unnamed: R21.2, U1.21
unnamed: R22.2, U1.9

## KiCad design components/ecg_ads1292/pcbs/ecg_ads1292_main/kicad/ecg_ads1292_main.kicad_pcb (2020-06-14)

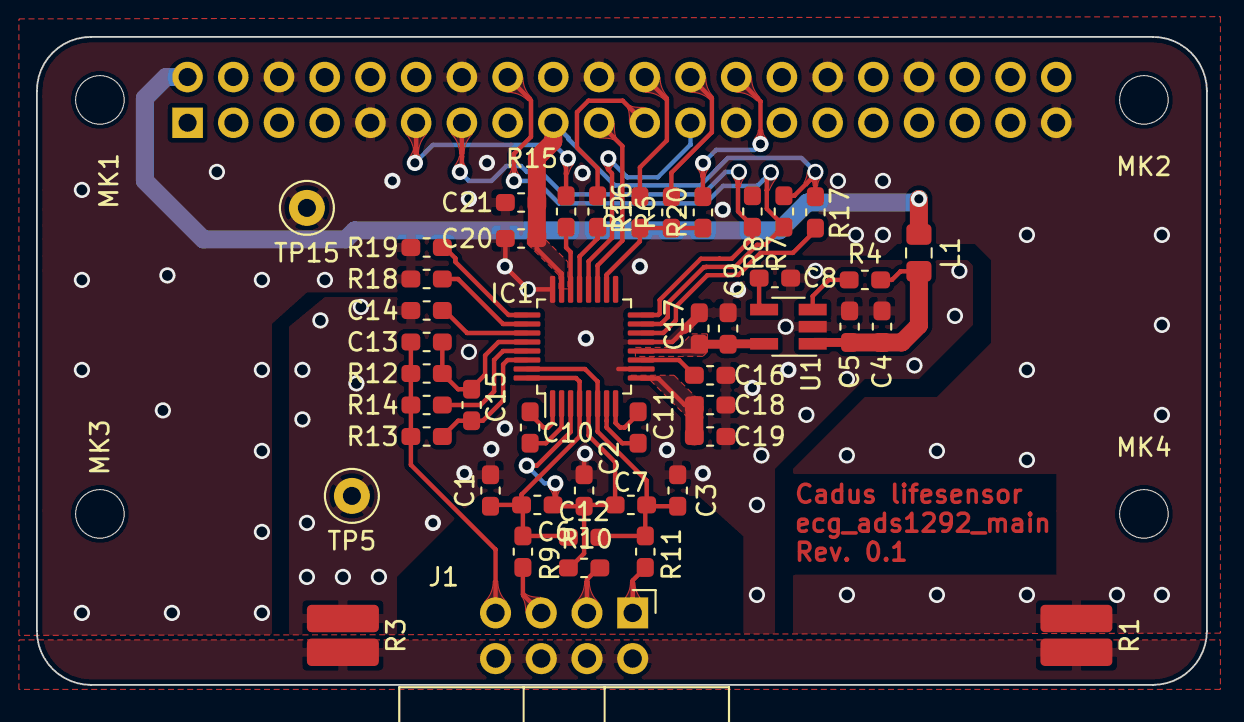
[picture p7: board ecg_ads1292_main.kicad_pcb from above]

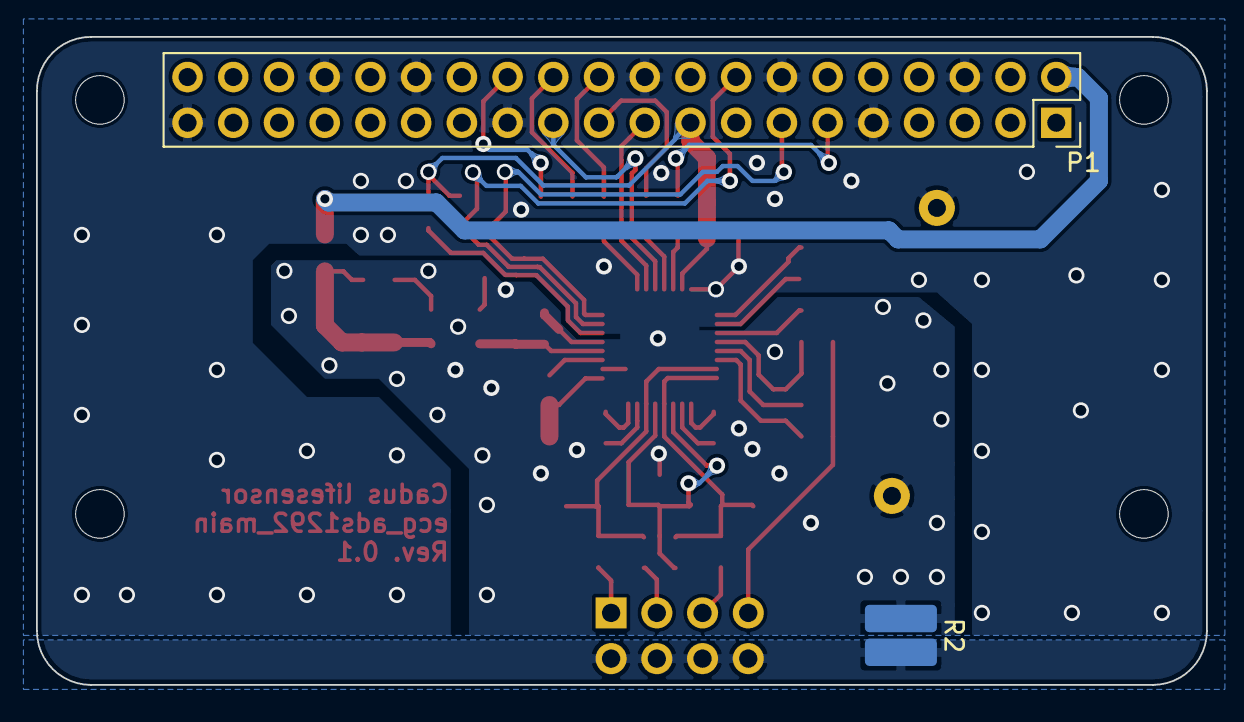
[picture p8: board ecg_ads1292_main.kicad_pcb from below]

Board: 2 copper layers, 65.0 x 36.0 mm, 52 parts (2 on the bottom side), 40 nets.

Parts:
C1, C2, C3: 3n 50V; C_0603_1608Metric_Pad1.05x0.95mm_HandSolder
C4, C9: 2.2u; C_0603_1608Metric_Pad1.05x0.95mm_HandSolder
C5, C17, C18, C20: 100n; C_0603_1608Metric_Pad1.05x0.95mm_HandSolder
C6, C7, C12: n.p.; C_0603_1608Metric_Pad1.05x0.95mm_HandSolder
C8: 10n; C_0603_1608Metric_Pad1.05x0.95mm_HandSolder
C10, C11: 4.7n; C_0603_1608Metric_Pad1.05x0.95mm_HandSolder
C13, C15: 470p 50V; C_0603_1608Metric_Pad1.05x0.95mm_HandSolder
C14, C16, C21: 1u; C_0603_1608Metric_Pad1.05x0.95mm_HandSolder
C19: 10u; C_0603_1608Metric_Pad1.05x0.95mm_HandSolder
IC1: ADS1292IPBSR; LQFP-32_5x5mm_P0.5mm
J1: Conn_02x04_Odd_Even; IDC-Header_2x04_P2.54mm_Horizontal
L1: MMZ2012R102AT000; L_0805_2012Metric_Pad1.15x1.40mm_HandSolder
MK1, MK2, MK3, MK4: n.p.; MountingHole_2.7mm_M2.5
P1: Conn_02x20_Odd_Even; PinSocket_2x20_P2.54mm_Vertical
R1, R2, R3: n.p.; R_0815_2038Metric_Pad1.53x4.00mm_HandSolder
R4, R6, R15, R16: 100; R_0603_1608Metric_Pad1.05x0.95mm_HandSolder
R5, R20: n.p.; R_0603_1608Metric_Pad1.05x0.95mm_HandSolder
R7, R8, R13, R17: 100k; R_0603_1608Metric_Pad1.05x0.95mm_HandSolder
R9, R10, R11: 22k; R_0603_1608Metric_Pad1.05x0.95mm_HandSolder
R12: 1M; R_0603_1608Metric_Pad1.05x0.95mm_HandSolder
R14, R18, R19: 6.8k; R_0603_1608Metric_Pad1.05x0.95mm_HandSolder
TP5, TP15: n.p.; TestPoint_Loop_D2.50mm_Drill1.0mm
U1: TPS73033DBVT; SOT-23-5_HandSoldering

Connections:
+3V3: C20.1, C21.1, IC1.23, P1.17, R7.2, R17.1
+5VA: L1.2, P1.2
/ECG_Sensor/3.3VA: C9.1, C17.1, IC1.12, U1.5
/ECG_Sensor/ads_in1_n: C2.1, C6.2, C7.1, IC1.3, IC1.5, R10.2
/ECG_Sensor/ads_in1_p: C1.1, C6.1, C12.1, IC1.4, IC1.32, R9.2
/ECG_Sensor/ads_in2_p: C3.1, C7.2, C12.2, IC1.6, IC1.31, R11.2
/LA: J1.5, R9.1
/LL: J1.1, R11.1
/RA: J1.3, R10.1
/RLD: C13.1, J1.7, R12.1, R13.1, R14.1
/SENS_INT_ECG: P1.11, R15.1
/SENS_MISO: P1.21, R16.1
/SENS_MOSI: IC1.19, P1.19
/SENS_SCLK: IC1.20, P1.23
/SENS_START: IC1.16, P1.13, R8.2
/~CS: IC1.18, R5.1, R6.1, R20.1
/~SENS_CS_BPM: P1.22, R5.2
/~SENS_CS_ECG: P1.24, R6.2
/~SENS_CS_SPO2: P1.26, R20.2
/~SENS_RST_ECG: IC1.15, P1.16, R7.1
GND: C1.2, C2.2, C3.2, C4.2, C5.2, C8.2, C9.2, C14.2, C16.2, C17.2, C18.2, C19.2, C20.2, C21.2, IC1.10, IC1.13, IC1.24, P1.6, P1.9, P1.14, P1.20, P1.25, P1.30, P1.34, P1.39, R1.1, R2.1, R3.1, R8.1, R18.2, R19.1, TP5.1, TP15.1, U1.2
GNDPWR: J1.2, J1.4, J1.6, J1.8, R1.2, R2.2, R3.2
unnamed: C4.1, C5.1, L1.1, R4.2, U1.1
unnamed: C8.1, U1.4
unnamed: C10.1, IC1.2
unnamed: C10.2, IC1.1
unnamed: C11.1, IC1.8
unnamed: C11.2, IC1.7
unnamed: C13.2, C15.2, IC1.28, R12.2
unnamed: C14.1, IC1.27
unnamed: C15.1, IC1.30, R13.2
unnamed: C16.1, IC1.11
unnamed: C18.1, C19.1, IC1.9
unnamed: IC1.14, R17.2
unnamed: IC1.21, R16.2
unnamed: IC1.22, R15.2
unnamed: IC1.25, R19.2
unnamed: IC1.26, R18.1
unnamed: IC1.29, R14.2
unnamed: R4.1, U1.3

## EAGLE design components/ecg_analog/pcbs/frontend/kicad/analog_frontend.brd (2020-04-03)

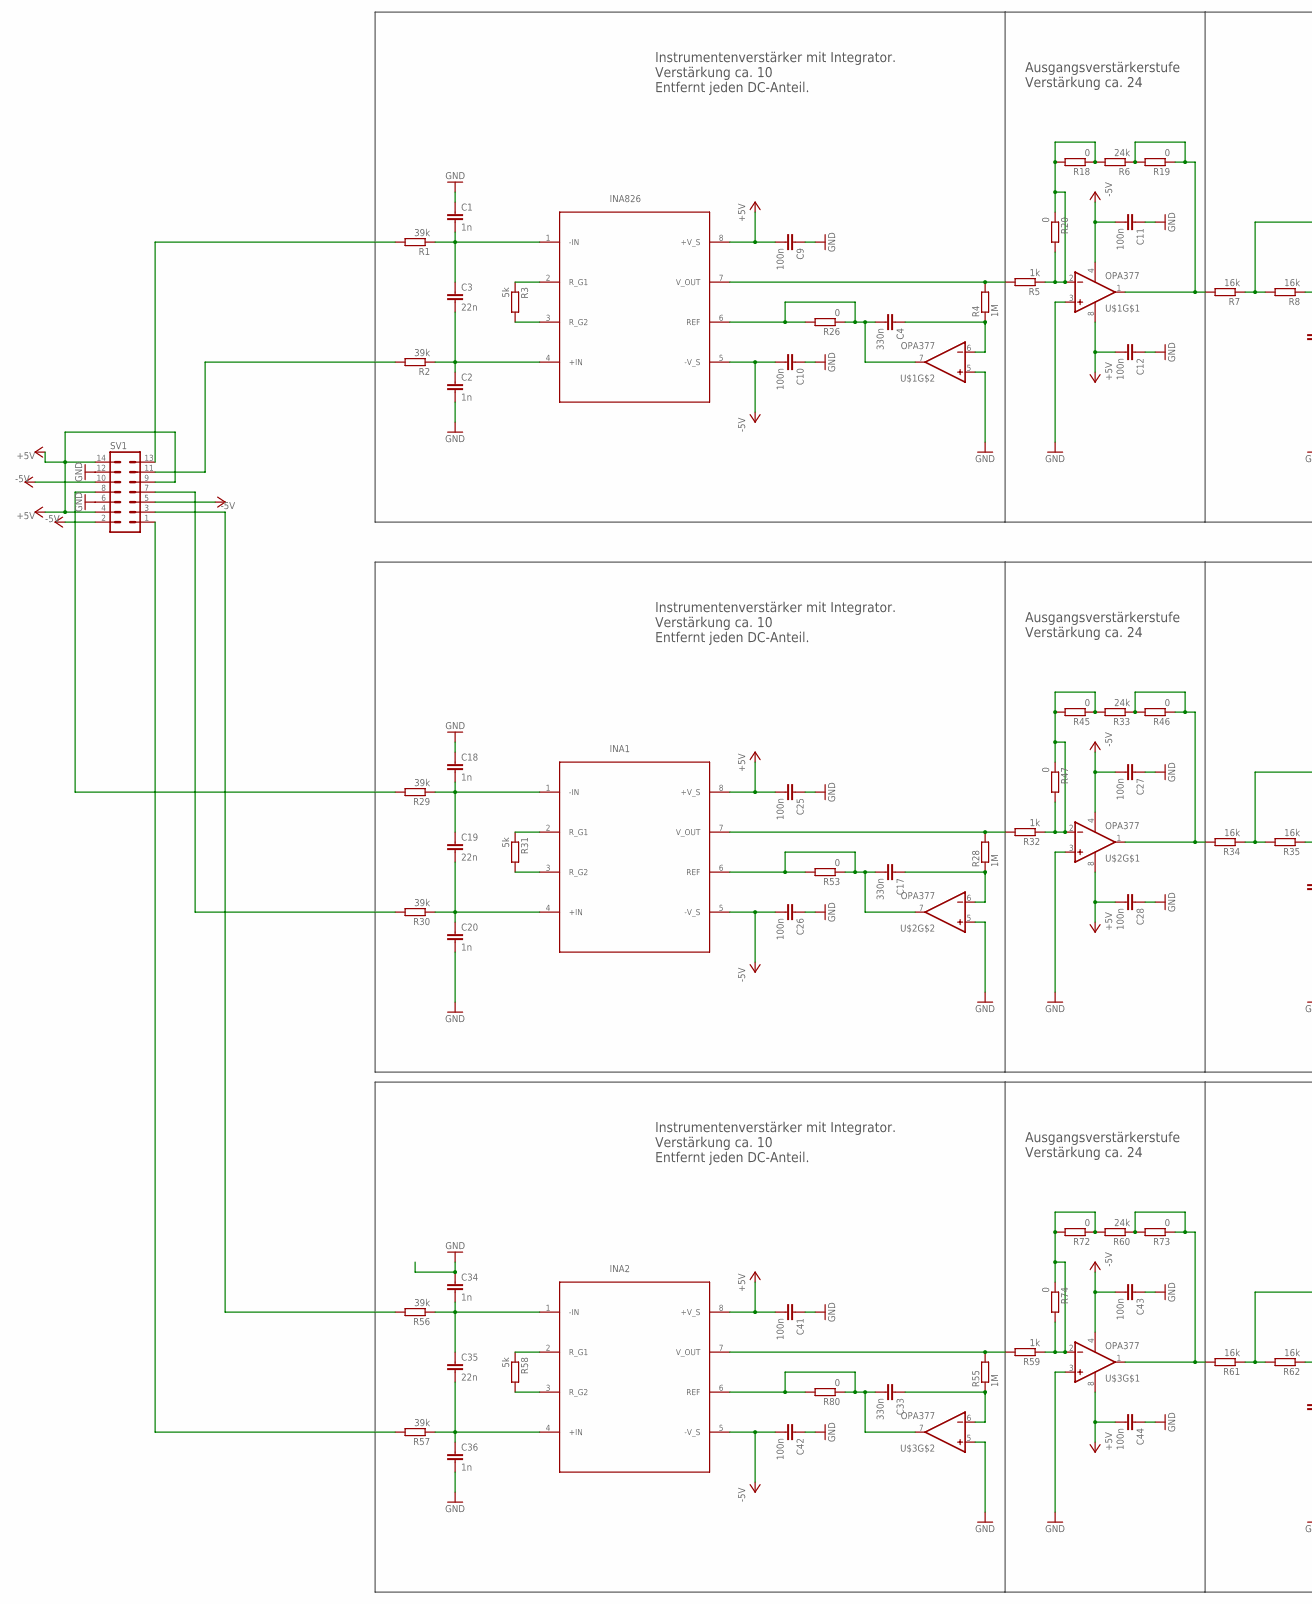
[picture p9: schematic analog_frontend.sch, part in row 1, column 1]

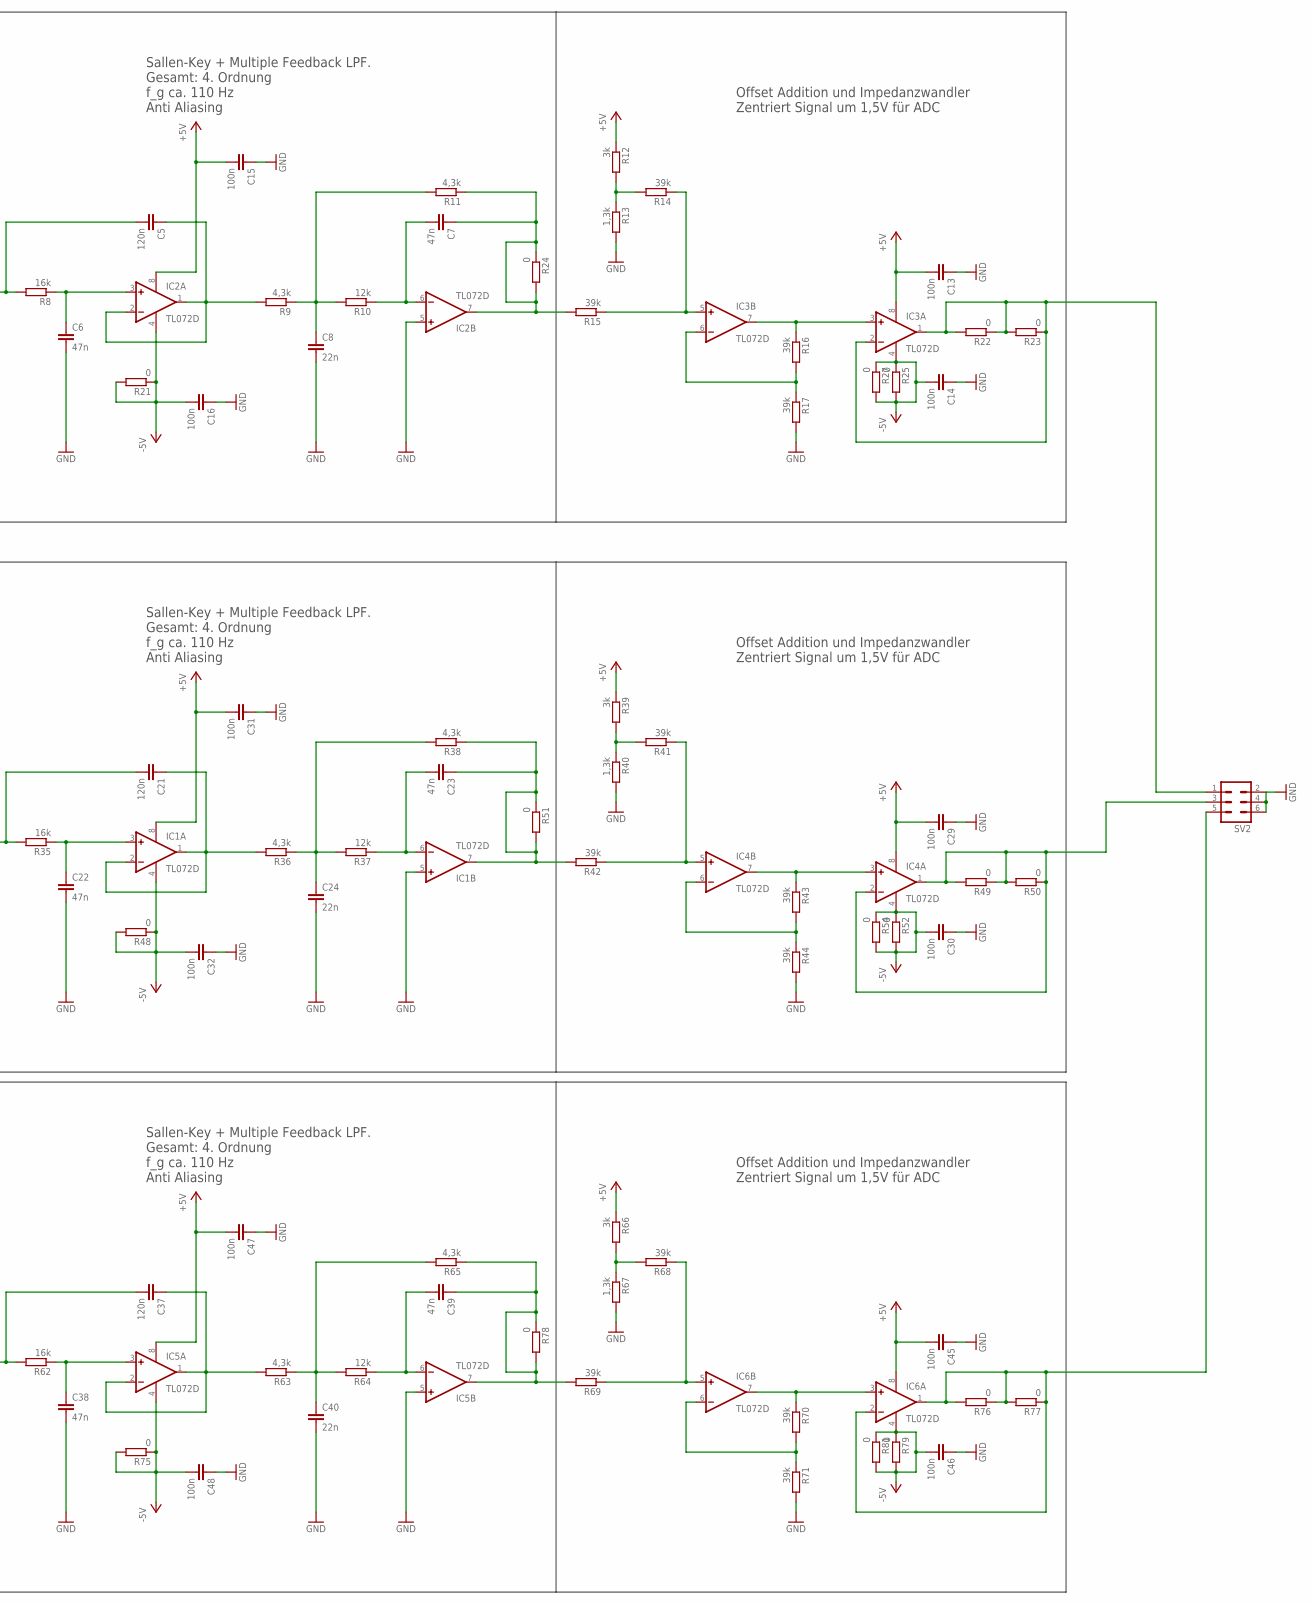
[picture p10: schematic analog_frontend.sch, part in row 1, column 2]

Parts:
C1, C2, C18, C20, C34, C36: 1n; C0805
C3, C8, C19, C24, C35, C40: 22n; C0805
C4, C17, C33: 330n; C1206
C5, C21, C37: 120n; C0805
C6, C7, C22, C23, C38, C39: 47n; C0805
C9, C10, C11, C12, C13, C14, C16, C25, C26, C27, C28, C29, C30, C32, C41, C42, C43, C44, C45, C46, C48: 100n; C0805
C15, C31, C47: 100n; C1206
IC1, IC2, IC3, IC4, IC5, IC6: TL072D; SO08
INA1, INA2, INA826: INA826; SOIC8
R1, R2, R14, R15, R16, R29, R30, R41, R42, R43, R56, R57, R68, R69, R70: 39k; R0805
R3, R31, R58: 5k; R0805
R4, R28, R55: 1M; R1206
R5, R32, R59: 1k; R1206
R6, R33, R60: 24k; R0805
R7, R34, R61: 16k; R1206
R8, R35, R62: 16k; R0805
R9, R11, R36, R38, R63, R65: 4,3k; R0805
R10, R37, R64: 12k; R0805
R12, R39, R66: 3k; R0805
R13, R40, R67: 1,3k; R1206
R17, R44, R71: 39k; R1206
R18, R19, R20, R21, R22, R23, R24, R25, R26, R27, R45, R46, R47, R48, R49, R50, R51, R52, R53, R54, R72, R73, R74, R75, R76, R77, R78, R79, R80, R81: 0; R1206
SV1: ML14L
SV2: ML6L
U$1, U$2, U$3: OPA377; SOIC8

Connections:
+5V: C9.2, C12.2, C13.2, C15.2, C25.2, C28.2, C29.2, C31.2, C41.2, C44.2, C45.2, C47.2, IC1.8 (V+), IC2.8 (V+), IC3.8 (V+), IC4.8 (V+), IC5.8 (V+), IC6.8 (V+), INA1.8 (+V_S), INA2.8 (+V_S), INA826.8 (+V_S), R12.1, R39.1, R66.1, SV1.4, SV1.9, SV1.14, U$1.8 (V+), U$2.8 (V+), U$3.8 (V+)
-5V: C10.2, C11.2, C14.2, C16.2, C26.2, C27.2, C30.2, C32.2, C42.2, C43.2, C46.2, C48.2, IC1.4 (V-), IC2.4 (V-), IC3.4 (V-), IC4.4 (V-), IC5.4 (V-), IC6.4 (V-), INA1.5 (-V_S), INA2.5 (-V_S), INA826.5 (-V_S), R21.1, R21.2, R25.1, R25.2, R27.1, R27.2, R48.1, R48.2, R52.1, R52.2, R54.1, R54.2, R75.1, R75.2, R79.1, R79.2, R81.1, R81.2, SV1.2, SV1.5, SV1.10, U$1.4 (V-), U$2.4 (V-), U$3.4 (V-)
GND: C1.1, C2.2, C6.2, C8.2, C9.1, C10.1, C11.1, C12.1, C13.1, C14.1, C15.1, C16.1, C18.1, C20.2, C22.2, C24.2, C25.1, C26.1, C27.1, C28.1, C29.1, C30.1, C31.1, C32.1, C34.1, C36.2, C38.2, C40.2, C41.1, C42.1, C43.1, C44.1, C45.1, C46.1, C47.1, C48.1, IC1.5 (+IN), IC2.5 (+IN), IC5.5 (+IN), R13.2, R17.2, R40.2, R44.2, R67.2, R71.2, SV1.6, SV1.12, SV2.2, SV2.4, SV2.6, U$1.3 (+IN), U$1.5 (+IN), U$2.3 (+IN), U$2.5 (+IN), U$3.3 (+IN), U$3.5 (+IN)
unnamed: C4.2, INA826.6 (REF), R26.1, R26.2, U$1.7 (OUT)
unnamed: C4.1, R4.1, U$1.6 (-IN)
unnamed: INA826.7 (V_OUT), R4.2, R5.2
unnamed: C1.2, C3.1, INA826.1 (-IN), R1.1
unnamed: C2.1, C3.2, INA826.4 (+IN), R2.1
unnamed: INA826.3 (R_G2), R3.2
unnamed: INA826.2 (R_G1), R3.1
unnamed: R5.1, R6.2, R18.1, R18.2, R20.1, R20.2, U$1.2 (-IN)
unnamed: R6.1, R7.2, R19.1, R19.2, U$1.1 (OUT)
unnamed: C5.2, R7.1, R8.2
unnamed: C5.1, IC2.1 (OUT), IC2.2 (-IN), R9.2
unnamed: C6.1, IC2.3 (+IN), R8.1
unnamed: C8.1, R9.1, R10.2, R11.2
unnamed: C7.2, IC2.6 (-IN), R10.1
unnamed: C7.1, IC2.7 (OUT), R11.1, R15.2, R24.1, R24.2
unnamed: IC3.5 (+IN), R14.1, R15.1
unnamed: IC3.6 (-IN), R16.2, R17.1
unnamed: R12.2, R13.1, R14.2
unnamed: IC3.3 (+IN), IC3.7 (OUT), R16.1
unnamed: IC3.1 (OUT), IC3.2 (-IN), R22.1, R22.2, R23.1, R23.2, SV2.1
unnamed: R1.2, SV1.13
unnamed: R2.2, SV1.11
unnamed: INA1.7 (V_OUT), R28.2, R32.2
unnamed: C17.1, R28.1, U$2.6 (-IN)
unnamed: C18.2, C19.1, INA1.1 (-IN), R29.1
unnamed: C19.2, C20.1, INA1.4 (+IN), R30.1
unnamed: INA1.3 (R_G2), R31.2
unnamed: INA1.2 (R_G1), R31.1
unnamed: C21.2, R34.1, R35.2
unnamed: C21.1, IC1.1 (OUT), IC1.2 (-IN), R36.2
unnamed: C22.1, IC1.3 (+IN), R35.1
unnamed: C24.1, R36.1, R37.2, R38.2
unnamed: C23.2, IC1.6 (-IN), R37.1
unnamed: C23.1, IC1.7 (OUT), R38.1, R42.2, R51.1, R51.2
unnamed: IC4.5 (+IN), R41.1, R42.1
unnamed: R39.2, R40.1, R41.2
unnamed: IC4.3 (+IN), IC4.7 (OUT), R43.1
unnamed: IC4.6 (-IN), R43.2, R44.1
unnamed: R32.1, R33.2, R45.1, R45.2, R47.1, R47.2, U$2.2 (-IN)
unnamed: IC4.1 (OUT), IC4.2 (-IN), R49.1, R49.2, R50.1, R50.2, SV2.3
unnamed: C17.2, INA1.6 (REF), R53.1, R53.2, U$2.7 (OUT)
unnamed: R33.1, R34.2, R46.1, R46.2, U$2.1 (OUT)
unnamed: R29.2, SV1.8
unnamed: R30.2, SV1.7
unnamed: INA2.7 (V_OUT), R55.2, R59.2
unnamed: C33.1, R55.1, U$3.6 (-IN)
unnamed: C34.2, C35.1, INA2.1 (-IN), R56.1
unnamed: C35.2, C36.1, INA2.4 (+IN), R57.1
unnamed: INA2.3 (R_G2), R58.2
unnamed: INA2.2 (R_G1), R58.1
unnamed: C37.2, R61.1, R62.2
unnamed: C37.1, IC5.1 (OUT), IC5.2 (-IN), R63.2
unnamed: C38.1, IC5.3 (+IN), R62.1
unnamed: C40.1, R63.1, R64.2, R65.2
unnamed: C39.2, IC5.6 (-IN), R64.1
unnamed: C39.1, IC5.7 (OUT), R65.1, R69.2, R78.1, R78.2
unnamed: IC6.5 (+IN), R68.1, R69.1
unnamed: R66.2, R67.1, R68.2
unnamed: IC6.3 (+IN), IC6.7 (OUT), R70.1
unnamed: IC6.6 (-IN), R70.2, R71.1
unnamed: R59.1, R60.2, R72.1, R72.2, R74.1, R74.2, U$3.2 (-IN)
unnamed: IC6.1 (OUT), IC6.2 (-IN), R76.1, R76.2, R77.1, R77.2, SV2.5
unnamed: C33.2, INA2.6 (REF), R80.1, R80.2, U$3.7 (OUT)
unnamed: R60.1, R61.2, R73.1, R73.2, U$3.1 (OUT)
unnamed: R56.2, SV1.3
unnamed: R57.2, SV1.1

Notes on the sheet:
Instrumentenverstärker mit Integrator. Verstärkung ca. 10 Entfernt jeden DC-Anteil.
Ausgangsverstärkerstufe Verstärkung ca. 24
Sallen-Key + Multiple Feedback LPF. Gesamt: 4. Ordnung f_g ca. 110 Hz Anti Aliasing
Offset Addition und Impedanzwandler Zentriert Signal um 1,5V für ADC

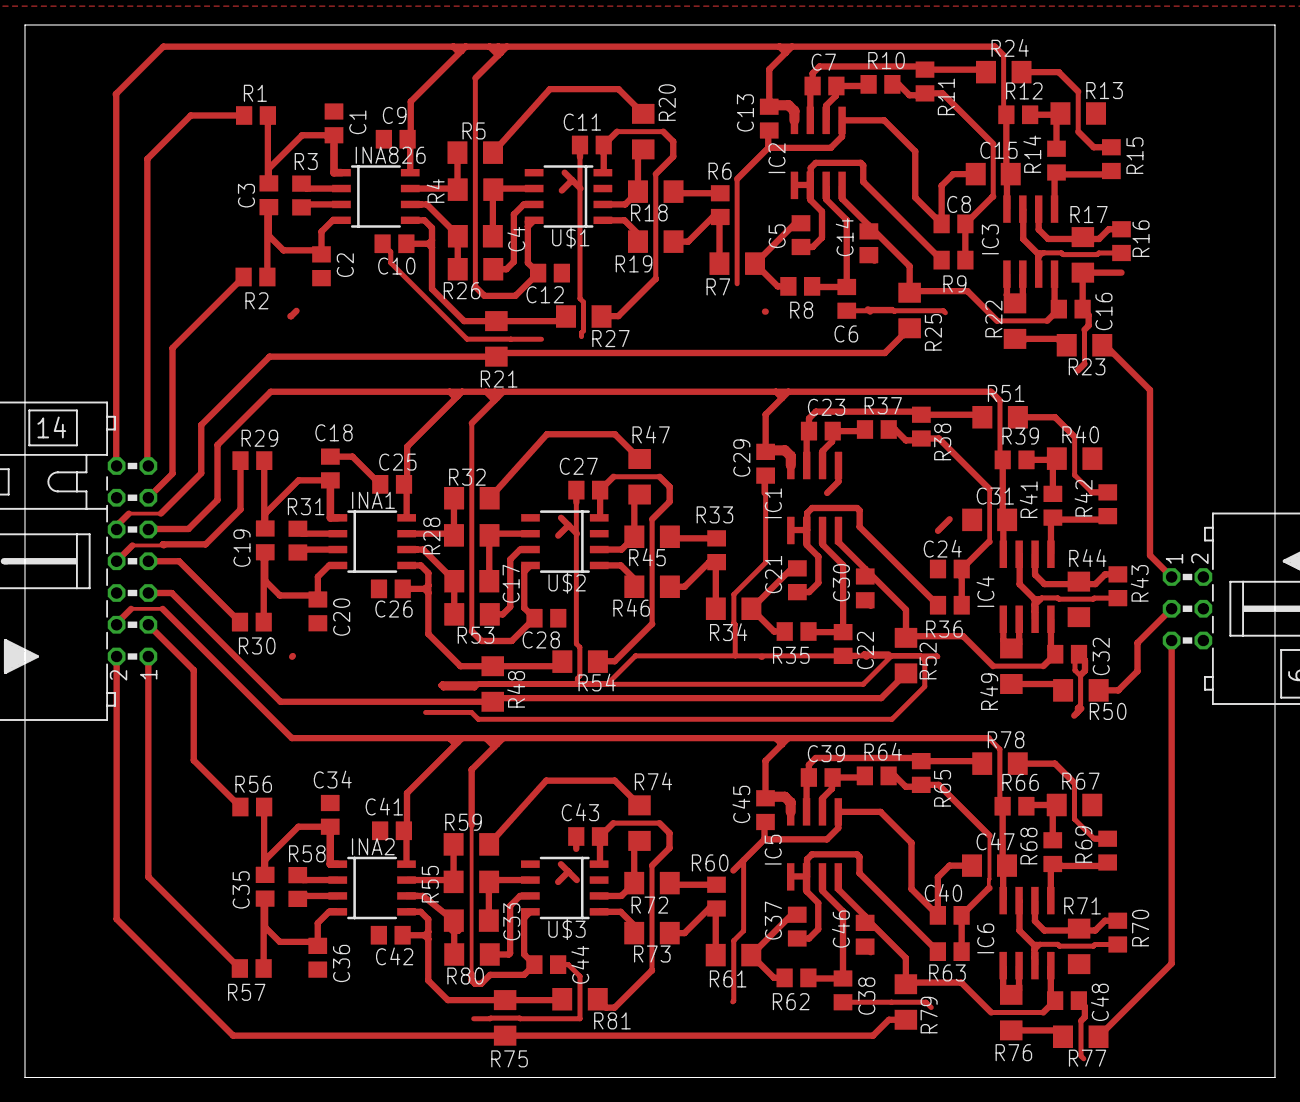
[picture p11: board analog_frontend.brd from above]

Board: 2 copper layers, 100.0 x 84.2 mm, 143 parts (0 on the bottom side), 69 nets.

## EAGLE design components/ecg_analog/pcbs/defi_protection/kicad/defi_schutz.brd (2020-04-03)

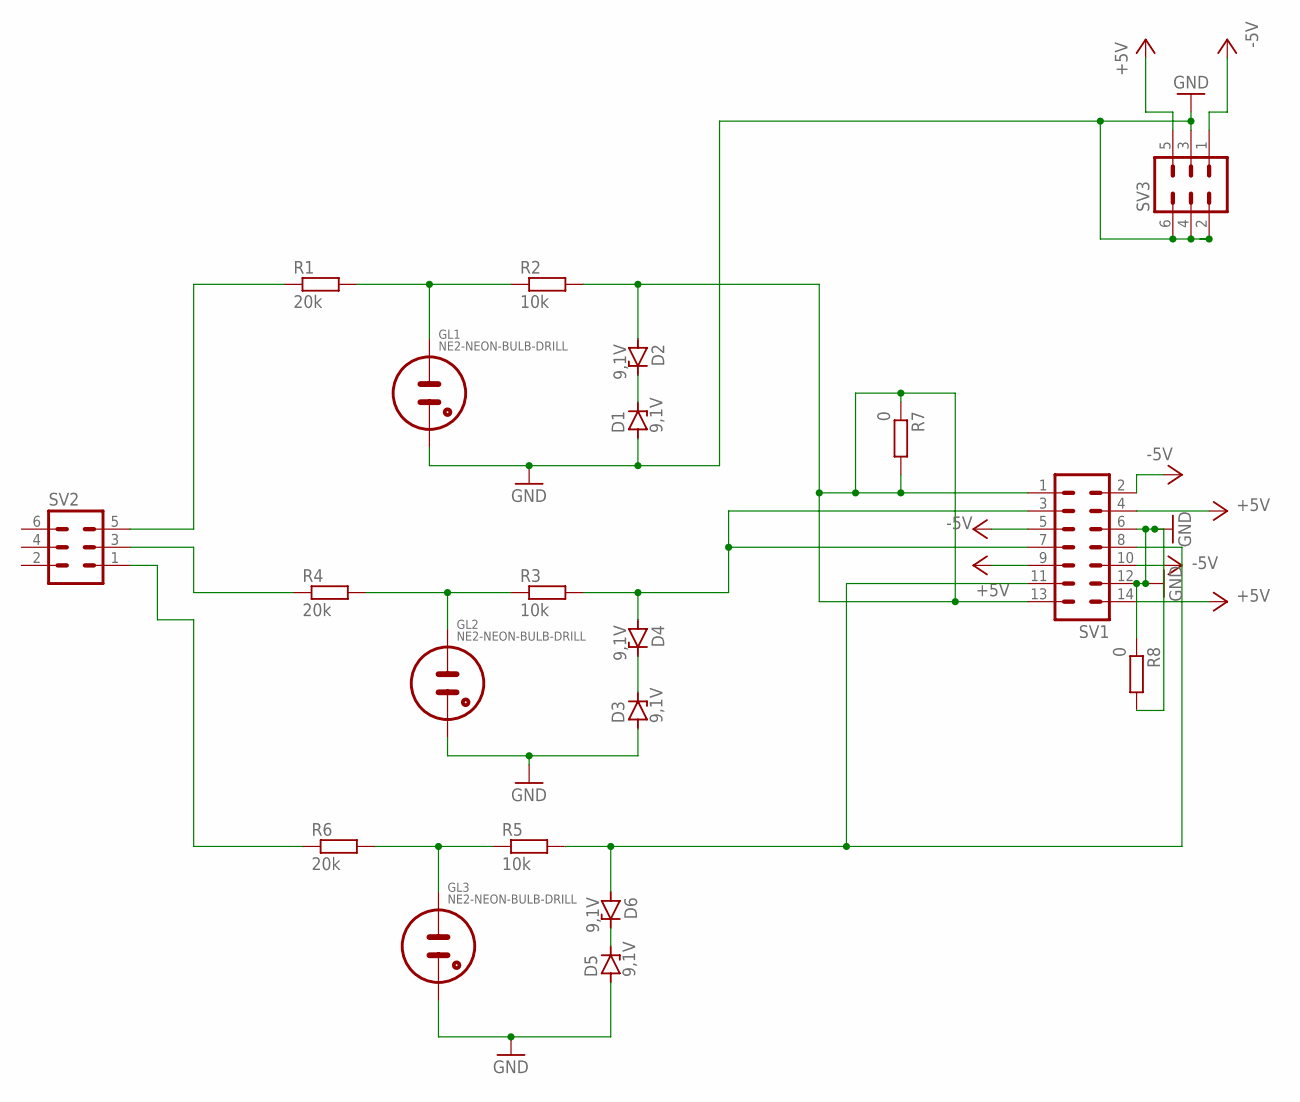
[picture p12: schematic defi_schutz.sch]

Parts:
D1, D2, D3, D4, D5, D6: 9,1V; DO41Z10
GL1, GL2, GL3: NE2-NEON-BULB-DRILL
R1, R4, R6: 20k; 0207/10
R2, R3, R5: 10k; 0207/10
R7, R8: 0; 0207/15
SV1: ML14L
SV2, SV3: ML6L

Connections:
+5V: SV1.4, SV1.9, SV1.14, SV3.5
-5V: SV1.2, SV1.5, SV1.10, SV3.1
GND: D1.A, D3.A, D5.A, GL1.2 (A1), GL2.2 (A1), GL3.2 (A1), R8.1, R8.2, SV1.6, SV1.12, SV3.2, SV3.3, SV3.4, SV3.6
unnamed: GL2.1 (A), R3.1, R4.2
unnamed: D4.A, R3.2, SV1.3, SV1.7
unnamed: D3.C, D4.C
unnamed: D1.C, D2.C
unnamed: GL1.1 (A), R1.2, R2.1
unnamed: D2.A, R2.2, R7.1, R7.2, SV1.1, SV1.13
unnamed: GL3.1 (A), R5.1, R6.2
unnamed: D6.A, R5.2, SV1.8, SV1.11
unnamed: D5.C, D6.C
unnamed: R1.1, SV2.5
unnamed: R4.1, SV2.3
unnamed: R6.1, SV2.1

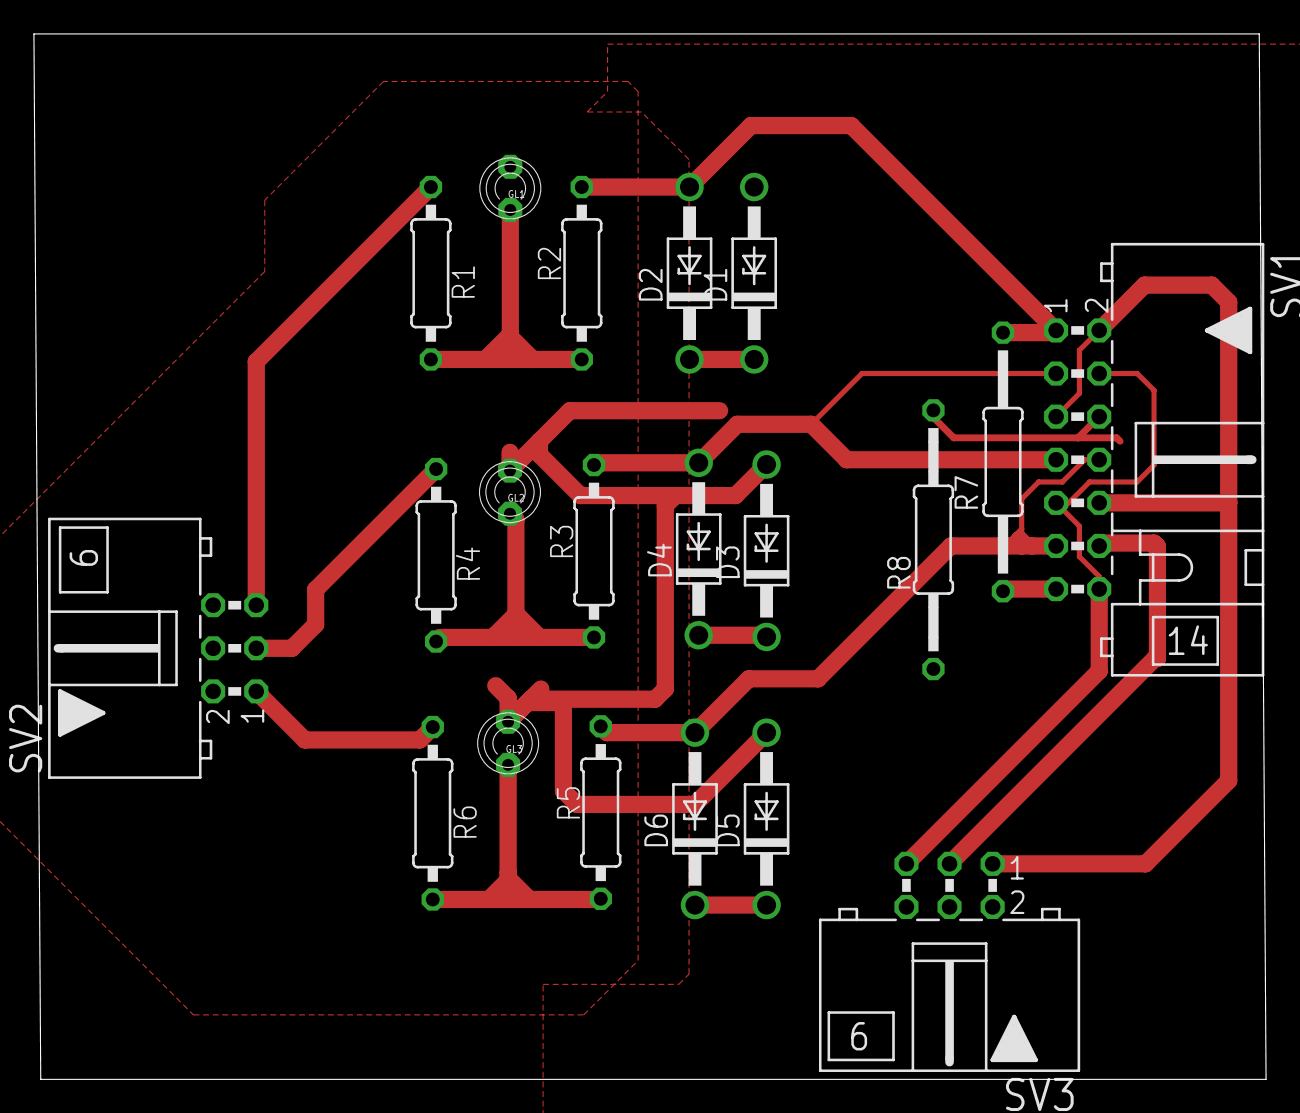
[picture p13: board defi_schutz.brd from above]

Board: 2 copper layers, 72.6 x 61.6 mm, 20 parts (0 on the bottom side), 15 nets.

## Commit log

2020-03-27 add kicad project for ecg
    [ecg_input_protection.sch, lifesensor-ecg.kicad_pcb, lifesensor-ecg.sch]
2020-03-28 first draft ecg protection
    [ecg_input_protection.sch, lifesensor-ecg.kicad_pcb, lifesensor-ecg.sch]
2020-04-03 update file structure
    [defi_protect.sch, ecg_ads1292_sensor.sch, ecg_input_protection.sch, egc_ads1292-B_Cu.gbr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]
2020-04-03 include analog frontend
    [analog_frontend.brd, analog_frontend.sch, defi_schutz.brd, defi_schutz.sch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]
2020-04-03 remove old ecg version
    [ecg_input_protection.sch, lifesensor-ecg.kicad_pcb, lifesensor-ecg.sch]
2020-04-11 allow daisy chaining and improve ground planes
    [egc_ads1292.kicad_pcb, egc_ads1292.sch]
2020-04-11 fix GND via not connected
    [egc_ads1292.kicad_pcb]
2020-04-11 simplify ads1292 supply scheme in schematic
    [ecg_ads1292_sensor.sch]
2020-04-15 orientation of pin headers in schematic matches pcb
    [ecg_ads1292_sensor.sch, egc_ads1292.kicad_pcb, egc_ads1292.sch]
2020-04-15 add gnd/gndpwr bridge at analog power supply
    [egc_ads1292.kicad_pcb, egc_ads1292.sch]
2020-04-15 add board name and version to pcb
    [egc_ads1292.kicad_pcb]
2020-04-15 add version and titles to schematic pages
    [ecg_ads1292_sensor.sch, ecg_input_protection.sch, egc_ads1292.sch]
2020-04-25 add system overview and pcb stack dimensions
2020-04-26 add templates for components and pcbs
    [COMPONENT_VARIANT_PCBNAME.kicad_pcb, COMPONENT_VARIANT_PCBNAME.sch]
2020-04-27 new ecg_ads1292 version based on template
    [defi_protect.sch, ecg_ads1292_main.kicad_pcb, ecg_ads1292_main.sch, ecg_ads1292_sensor.sch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]
2020-04-27 schematic passes erc with two accpted warnings
    [ecg_ads1292_main.sch, ecg_ads1292_sensor.sch]
2020-04-27 schematic passes checklist
    [ecg_ads1292_main.sch]
2020-04-27 the layout passes the checklist
    [ecg_ads1292_main.kicad_pcb]
2020-04-27 update check lists
    [COMPONENT_VARIANT_PCBNAME.kicad_pcb, COMPONENT_VARIANT_PCBNAME.sch]
2020-04-27 add gerber files
    [ecg_ads1292_main-B_Cu.gbl, ecg_ads1292_main-B_Mask.gbs, ecg_ads1292_main-B_SilkS.gbo, ecg_ads1292_main-Edge_Cuts.gm1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]
2020-04-27 add board svg image
    [ecg_ads1292_main.kicad_pcb]
2020-04-28 ignore schematic library cache in pcb template
2020-04-28 add chip select mux in pcb template
    [COMPONENT_VARIANT_PCBNAME.kicad_pcb, COMPONENT_VARIANT_PCBNAME.sch]
2020-04-28 add chip select mux in ads1292_main schematics
    [ecg_ads1292_main.sch, ecg_ads1292_sensor.sch]
2020-04-28 add chip select mux on ads1292_main pcb
    [ecg_ads1292_main-B_Cu.gbl, ecg_ads1292_main-B_Mask.gbs, ecg_ads1292_main-B_SilkS.gbo, ecg_ads1292_main-Edge_Cuts.gm1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]
2020-04-29 fix project templates in pcb checklist
2020-05-07 add defiprotect_gdt component
    [defiprotect_gdt_main.kicad_pcb, defiprotect_gdt_main.sch]
2020-05-07 ecg_ads1292: fix symbol library paths
    [ecg_ads1292_main.kicad_pcb, ecg_ads1292_main.sch, ecg_ads1292_sensor.sch]
2020-05-07 add teardrops to layout
    [ecg_ads1292_main.kicad_pcb]
2020-05-07 ecg_ads1292 improve input filter circuit
    [ecg_ads1292_main.kicad_pcb, ecg_ads1292_sensor.sch]
2020-05-07 ecg_ads1292: improve power supply ferrit bead layout
    [ecg_ads1292_main.kicad_pcb]
2020-05-07 ecg_ads1292: remove obsolete pcb directory
    [egc_ads1292.kicad_pcb]
2020-05-29 ecg_ads1292: update part fields
    [ecg_ads1292_main.sch, ecg_ads1292_sensor.sch]
2020-05-31 ecg_ads1292: update schematic date
    [ecg_ads1292_main.sch, ecg_ads1292_sensor.sch]
2020-05-31 ecg_ads1292: layout checklist passed
    [ecg_ads1292_main-B_Cu.gbl, ecg_ads1292_main-B_Mask.gbs, ecg_ads1292_main-B_SilkS.gbo, ecg_ads1292_main-Edge_Cuts.gm1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]
2020-06-14 include board view svg instead of png in ads1292 README
2020-06-14 update parts and add digikey PNs
    [ecg_ads1292_main.sch, ecg_ads1292_sensor.sch]
2020-06-14 update parts in pcb
    [ecg_ads1292_main.kicad_pcb]
2020-07-04 add ecg ads1292 pin/signal description to docs
2020-07-07 move templates into common subdirectory
    [COMPONENT_VARIANT_PCBNAME.kicad_pcb, COMPONENT_VARIANT_PCBNAME.sch]
2020-07-25 archive all components
    [ecg_ads1292_main.sch]
2020-08-25 improve pcb template
    [COMPONENT_VARIANT_PCBNAME.kicad_pcb, COMPONENT_VARIANT_PCBNAME.sch]
2020-08-25 board name defaults to None when creating a Settings object using python version below 3.7
2020-08-25 create new component esp32_devkitc
    [esp32_devkitc_main.kicad_pcb, esp32_devkitc_main.sch]
2020-08-25 Add ESP32 DevKit-C symbol and footprint from snap eda
2020-08-25 add devkitc to board
    [esp32_devkitc_main.kicad_pcb, esp32_devkitc_main.sch]
2020-10-13 add ESP32, WROOM32, DEVKIT-C data sheets
2020-10-13 [WIP] develop ESP32-main pcb
    [esp32_devkitc_main.kicad_pcb, esp32_devkitc_main.sch]
2020-10-13 add system overview to esp32 docs
2020-10-13 updates temp
    [esp32_devkitc_main.kicad_pcb]
2020-10-13 adds TODOs
    [esp32_devkitc_main.sch]
2020-11-01 updates TODOs
    [esp32_devkitc_main.sch]
2020-11-01 updates pinout of esp32 devkitc, adds pinout odt document
    [esp32_devkitc_main.sch]
2020-11-13 first drafted routing, WARNING: JTAG TCK missing!
    [esp32_devkitc_main.kicad_pcb, esp32_devkitc_main.sch]
2020-11-14 adds todos and notes
    [esp32_devkitc_main.kicad_pcb, esp32_devkitc_main.sch]
2020-11-22 Ready for review! fixes JTAG, adds updated pinout, updates JTAG header docu in Development_esp32_devkitc, finishes routing, adds JTAG resistors according to ESP32 manual
    [esp32_devkitc_main.kicad_pcb, esp32_devkitc_main.sch]
2020-11-24 small cleanup
    [esp32_devkitc_main.kicad_pcb]
2020-12-01 small update
    [esp32_devkitc_main.kicad_pcb, esp32_devkitc_main.sch]
2020-12-01 moves R21 below devkit
    [esp32_devkitc_main.kicad_pcb]
2020-12-01 Move FB1 closer to interconnect
    [esp32_devkitc_main.kicad_pcb]
2020-12-01 removes filling
    [esp32_devkitc_main.kicad_pcb]
2020-12-01 remove fillings for merge
    [esp32_devkitc_main.kicad_pcb]
2020-12-05 adds gpio expander, WIP
    [PCF8574ADWR.step, esp32_devkitc_main.kicad_pcb, esp32_devkitc_main.sch]
2020-12-05 updates 5V jack, adds jumpers for I2C GPIO Expander Adress, updates pinout, updates docs
    [esp32_devkitc_main.kicad_pcb, esp32_devkitc_main.sch]
2020-12-08 improve GND return paths for display SPI signals
    [esp32_devkitc_main.kicad_pcb, esp32_devkitc_main.sch]
